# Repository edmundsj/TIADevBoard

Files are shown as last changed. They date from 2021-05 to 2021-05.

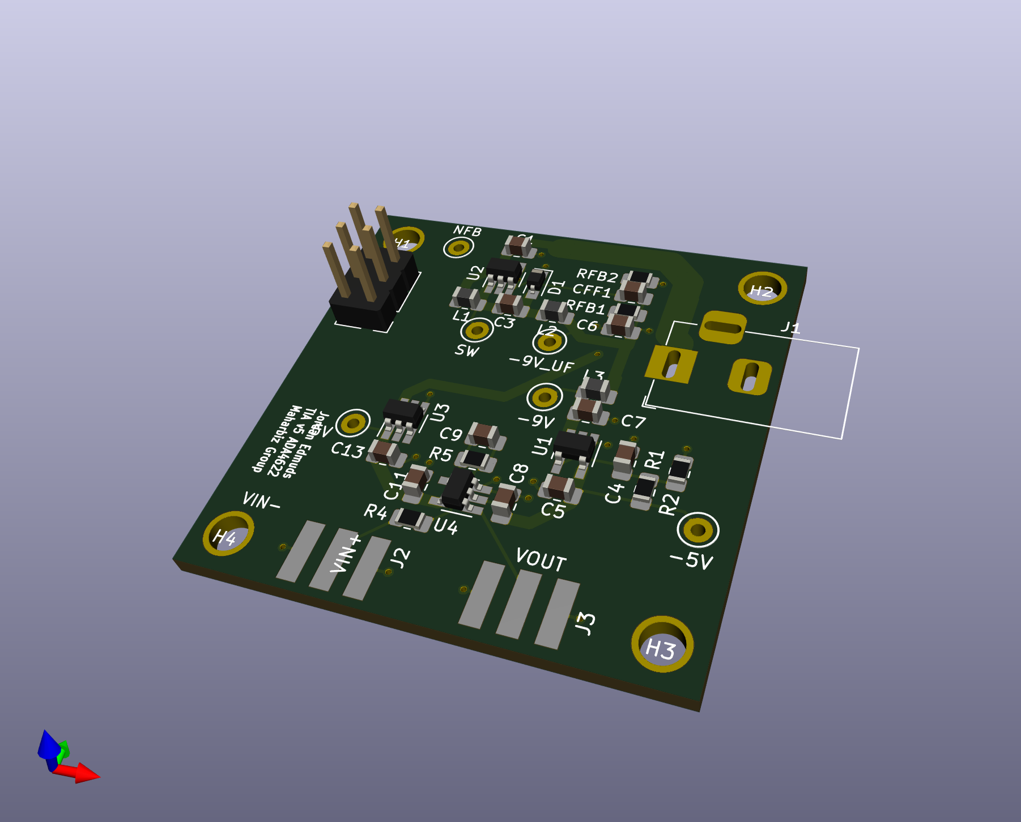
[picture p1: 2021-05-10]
tia_dev_board_3D.png

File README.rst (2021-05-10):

+/-5V TIA Dev Board
=========================

Features
----------
- On-board +/-5V supply generation
- Uses a low-noise opamp: ADA4622 (<1fA/rtHz, <15nV/rtHz)
- Low bias current opamp (<10pA) for accurate DC current measurement
- Opamp is unity gain stable, no input offset (<2uV), common-mode input beyond the rails, R2R output
- SMA input and output
- Low parasitic input/output capacitance

Issues in Versions 1,2
-----------------------
- [FIXED in v3] Old versions of this PCB relied on an off-board +/-15V dual supply, which was coupling in a huge amount of noise into the opamp.
- [FIXED in v3] Old opamp (ADA4625) appears to be often out of stock and is quite expensive (~$10). 

Issues in Version 3
--------------------
- The screw terminal is exerting force on an unspported area of the PCB, I should add another couple of standoffs so this does not happen.
- The -5V input is actually -7.5V. Should use two 3k resistors instead of two 1k resistors
- [FIXED v4] Pin 2 (sense pin) on ADP7183 is not connected to anything. It should be connected to Vout.
- [FIXED v4] There should be a 1uF capacitor to ground hanging off pin VA.
- [FIXED v4] There should be a 10nF capacitor between VA and VFB, not 1uF.

Issues in Version 4
---------------------
- [FIXED v5] Very high output noise (~10uV/rtHz) when driving diode with opamp. Switched to driving with GND.
- [FIXED v5] OPA2387 appears to have ~5x the specced current noise. Switched to ADA4622 (0.7fA/rtHz vs 70). 
- [FIXED v5] Switch back to dual supply with linear regulators
- [FIXED v5] Filter the output of the switched supply with an CLC network
- [FIXED v5] Add bulkhead-mount input/output SMA connectors to enclose entire board in grounded Faraday cage

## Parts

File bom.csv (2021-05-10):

Part Name | Reference | Value | Quantity
Capacitor | C3 | 1uF | 1
Capacitor | C4 | 10nF | 1
Capacitor | C9 | 3pF | 1
Capacitor | C8, C11 | 100nF | 2
Capacitor | C1, C5-C7, C13 | 10uF | 5
Capacitor | CFF1 | 100pF | 1
Diode | D1 | - | 1
DC Jack | J1 | - | 1
SMA Connector | J2, J3 | - | 2
Ground connector | J4 | - | 1
Inductor | L1-L3 | 22uH | 3
Resistor | R1 | 100k | 1
Resistor | R2 | 32k | 1
Resistor | R4 | 0R | 1
Resistor | R5 | 1M | 1
Resistor | RFB1 | 30k | 1
Resistor | RFB2 | 4.7k | 1
Negative regulator | U1 | TPS723 | 1
Boost converter | U2 | LM2611 | 1
5V regulator | U3 | ADP3330-5 | 1
Opamp | U4 | ADA4622 | 1

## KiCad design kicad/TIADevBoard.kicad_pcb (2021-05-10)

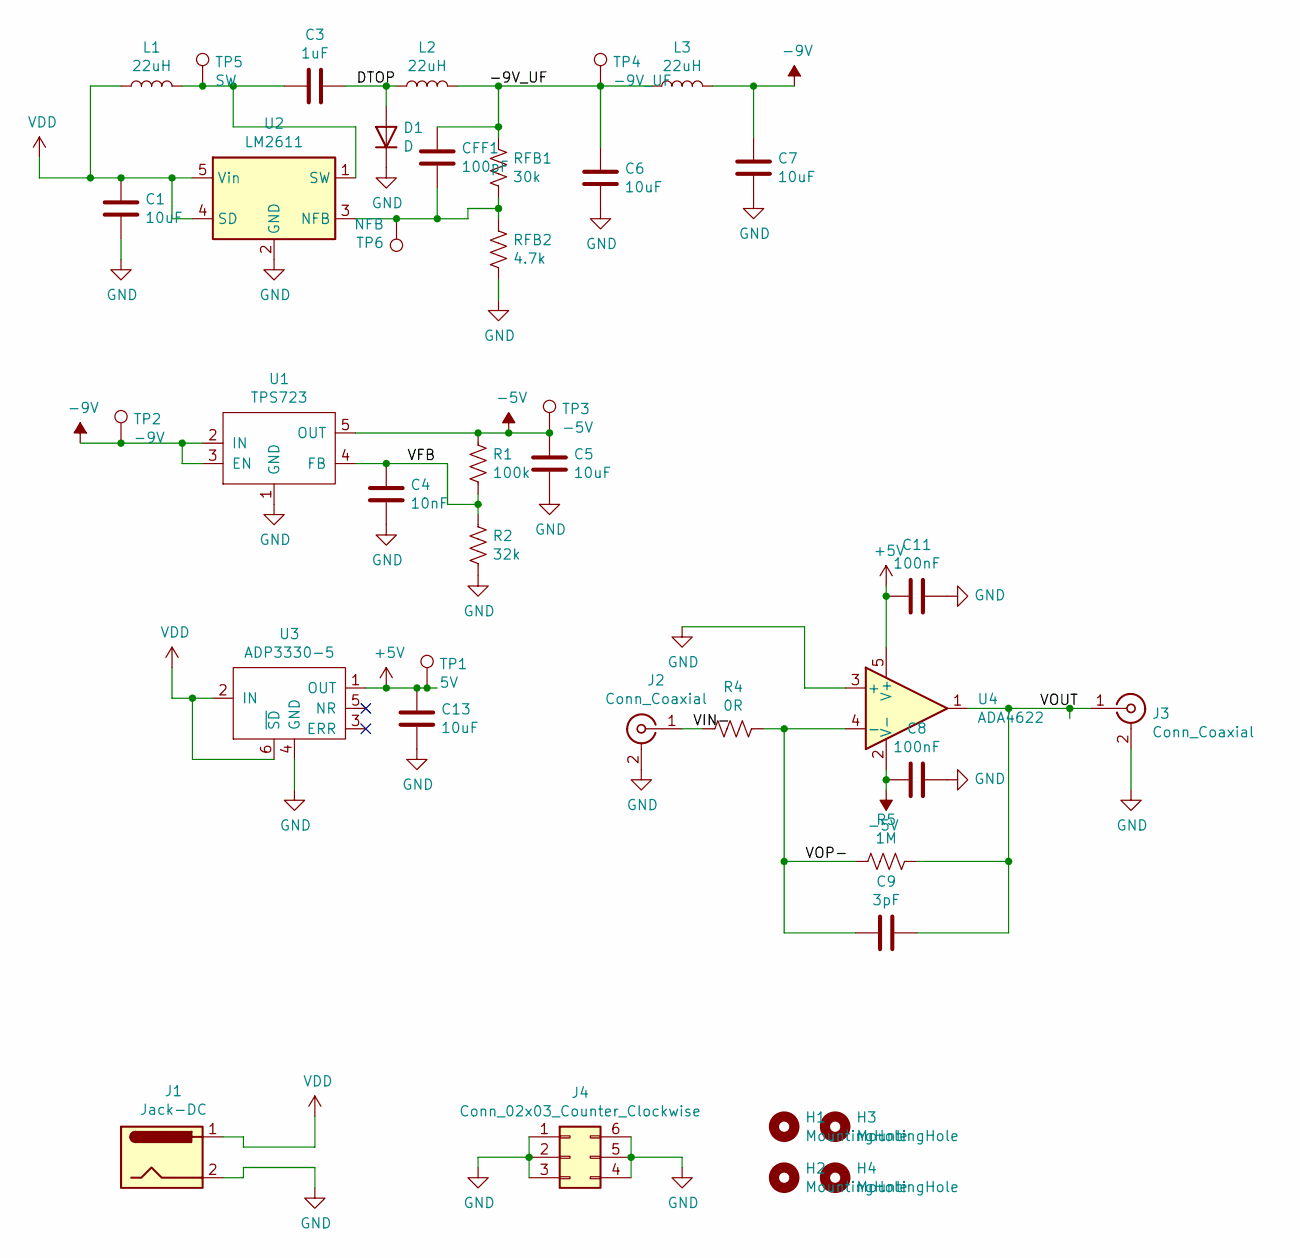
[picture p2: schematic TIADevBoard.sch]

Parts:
C1, C5, C6, C7, C13: 10uF; C_0805_2012Metric_Pad1.15x1.40mm_HandSolder
C3: 1uF; C_0805_2012Metric_Pad1.15x1.40mm_HandSolder
C4: 10nF; C_0805_2012Metric_Pad1.15x1.40mm_HandSolder
C8, C11: 100nF; C_0805_2012Metric_Pad1.15x1.40mm_HandSolder
C9: 3pF; C_0805_2012Metric_Pad1.15x1.40mm_HandSolder
CFF1: 100pF; C_0805_2012Metric_Pad1.15x1.40mm_HandSolder
D1: D; D_SOD-323_HandSoldering
H1, H2, H3, H4: MountingHole; m3_mounting_hole
J1: Jack-DC; BarrelJack_Horizontal
J2, J3: Conn_Coaxial; CON-SMA-EDGE-S
J4: Conn_02x03_Counter_Clockwise; PinHeader_2x03_P2.54mm_Vertical
L1, L2, L3: 22uH; L_0805_2012Metric_Pad1.15x1.40mm_HandSolder
R1: 100k; R_0805_2012Metric_Pad1.15x1.40mm_HandSolder
R2: 32k; R_0805_2012Metric_Pad1.15x1.40mm_HandSolder
R4: 0R; R_0805_2012Metric_Pad1.15x1.40mm_HandSolder
R5: 1M; R_0805_2012Metric_Pad1.15x1.40mm_HandSolder
RFB1: 30k; R_0805_2012Metric_Pad1.15x1.40mm_HandSolder
RFB2: 4.7k; R_0805_2012Metric_Pad1.15x1.40mm_HandSolder
TP1: 5V; TestPoint_Keystone_5000-5004_Miniature
TP2: -9V; TestPoint_Keystone_5000-5004_Miniature
TP3: -5V; TestPoint_Keystone_5000-5004_Miniature
TP4: -9V_UF; TestPoint_Keystone_5000-5004_Miniature
TP5: SW; TestPoint_Keystone_5000-5004_Miniature
TP6: NFB; TestPoint_Keystone_5000-5004_Miniature
U1: TPS723; SOT-23-5_HandSoldering
U2: LM2611; SOT-23-5_HandSoldering
U3: ADP3330-5; SOT-23-6_Handsoldering
U4: ADA4622; SOT-23-5_HandSoldering

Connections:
+5V: C11.2, C13.1, TP1.1, U3.1 (OUT), U4.5 (V+)
-5V: C5.1, C8.2, R1.1, TP3.1, U1.5 (OUT), U4.2 (V-)
-9V: C7.1, L3.2, TP2.1, U1.2 (IN), U1.3 (EN)
/-9V_UF: C6.1, CFF1.1, L2.2, L3.1, RFB1.1, TP4.1
/DTOP: C3.1, D1.2 (A), L2.1
/VFB: C4.1, R1.2, R2.1, U1.4 (FB)
/VIN-: J2.1 (In), R4.2
/VOP-: C9.2, R4.1, R5.2, U4.4 (-)
/VOUT: C9.1, J3.1 (In), R5.1, U4.1
GND: C1.2, C4.2, C5.2, C6.2, C7.2, C8.1, C11.1, C13.2, D1.1 (K), J1.2, J2.2 (Ext), J3.2 (Ext), J4.1, J4.2, J4.3, J4.4, J4.5, J4.6, R2.2, RFB2.2, U1.1 (GND), U2.2 (GND), U3.4 (GND), U4.3 (+)
unnamed: C3.2, L1.2, TP5.1, U2.1 (SW)
unnamed: CFF1.2, RFB1.2, RFB2.1, TP6.1, U2.3 (NFB)
VDD: C1.1, J1.1, L1.1, U2.4 (SD), U2.5 (Vin), U3.2 (IN), U3.6 (~SD)

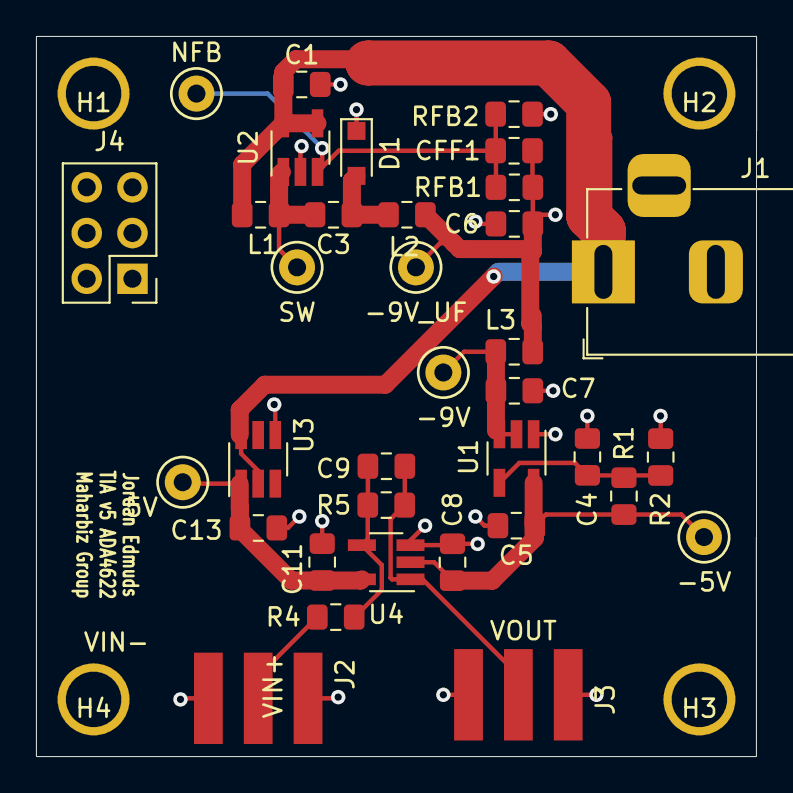
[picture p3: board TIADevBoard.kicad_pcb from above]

Board: 2 copper layers, 40.0 x 40.0 mm, 39 parts (0 on the bottom side), 13 nets.

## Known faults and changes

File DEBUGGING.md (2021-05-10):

# Appendix 1 - Debugging Notes
- I'm pretty sure I fried my -2.5V regulator. With an input of -3.44V, it outputs -1.97V. This is a 1.5V dropout voltage with a target regulation of -2.5V, which indicates I destroyed the thing. It's also completely contaminated with switching noise of magnitude ~40mVpp, which means we aren't regulaating anything. The switching noise at the output of the switching regulator is 120mVpp, and the switching frequency is 6.58kHz. This switching speed seems really low - it would seem to indicate we have a ~3nF timing capacitor, but we have a ~200pF capacitor.
- I will try replacing C7 with a 10nF capacitor and short pin 1 to pin 2, see if that fixes the issues I was having.
- Still getting oscillation when replacing C7 with a 47nF cap and shorting pin 1 and pins 2, although the oscillations are at a much higher frequency (~10x compared to before). I suspect the capacitance value has something to do with this. I added a 1uF capacitor between pin 3 (VA) and ground, connected via a jumper wire. Adding this capacitor caused the oscillations to stop, but the output voltage is -3.3V, not -2.5V, and the regulation is absolute shit. The datasheet says that C7 can be between 10nF and 1uF, so I don't think that's the issue. I think I may just give up on the negative supply. VREG should be at -0.5V but it appears to not be at that voltage, it's actually like 50mV.
- I suspect this has something to do with either the rework conditions (worked at too high of a temperature) or I accidentally ESD'd the chip.
- It may be advisable to switch to just driving the shield to the photodiode with the opamp rather than grounding the shield. Before redesigning the PCB to that effect, I'll try to solder on one more more tomorrow, paying close attention to rework temperature, keeping the rework temperature under 500F, and always keeping myself grounded to avoid frying the chip. That would save considerably on complexity of the PCB and I wouldn't have to use any of these godforsaken QFN packages. The downside is higher impedance driving the shield, but I think that should be fine.
- If the opamp has a biased output (for example at 1.65V) this means that the following stage will need a different offset voltage to bias the ADC properly - that's OK, I can increase the offset from VDD/4 to VDD/2 and this issue should be fixed. This opamp also may not behave properly when driving the cable capacitance. It should work, as I don't expect the parasitic cap to be more than ~100pF. A single supply would work for this just fine, with some voltage division. Yeah, let's just do that.
- Well, at least the voltage inverter worked decently well :) Nowhere close to spec, but it still inverted the voltage.
- We should test the opamp tomorrow to confirm it works as expected.
- The new TIA has higher noise than expected (400nV/rtHz), and, when connected to the photodiode, the noise goes up MASSIVELy to around 60uV/rtHz, even after ensuring the ADC is properly biased. I don't know what the issue is, but it's pretty bad. The guard voltage is correct (1.5V), and the voltage across the diode is very nearly 0V. Less than ~1mV. Either the photodiode does not like being biased in this way, or the TIA is just a heaping pile of shit. I guess for now I'm stuck with my old TIA, as I have no idea what's going on with this one. The 60Hz interferers are still there, indicating the noise is not coming intermittently from the power supply. However, the interferers are completely eliminated by a crappy Faraday cage, which I never achieved with the last TIA. 
- Here's my guess as to why the noise is so high: the output current noise of the opamp is being dropped across the photodiode, which has a very high impedance. If the photodiode were a dummy load with a lower impedance, this would not be the case. The output current noise would only have to be in the ~pA/rtHz range, which is potentially plausible. I can connect a dummy load tomorrow to see if this is indeed the issue. If it is, I'm going to need to rethink how to use a negative supply for this, and how to add a reliable (integrated) Faraday cage to my PCB, completely covering the high-impedance node.
- Apparently what I am really looking for is now a low-noise opamp per se, since this usually means low VOLTAGE noise, but a low input bias current opamp (which implies low current noise). However, the OPA2387 is rated for a bias current of 135pA, which would predict an input current noise density of 7fA/rtHz, which is nowhere close to its spec. Apparently also JFET-based opamps are what I am looking for. This is how I should start my search. I also want an opamp that's specced at the same supply voltages I am plannong on using, and at this point, I'm flexible.
- Ultimately, my problem is that I want an opamp which can operate off a 5V supply (or anywhere near 5V) so I can use a positive and negative supply. The ADA4625 does not work for this because it requires the input common-mode voltage to be 1.5V, not VDD/2, and the output voltage to be VDD/2, which is clearly not tenable if I am operating it as a TIA. It looks like the ADA4622 is an excellent choice. 0.8fA/rtHz current noise, specced at +/-5V operation, 12nV/rtHz voltage noise, and works at Vcm=0V. PSRR is only 80dB, but that's a minimum guaranteed spec, so I'll work with it.
- I found this app note on noise to be quite helpful: https://www.analog.com/media/en/training-seminars/tutorials/MT-047.pdf
- Analog devices recommends using the ADP5070 as the switching regulator, which operates at a whopping 2MHz. Why do they recommend this? What's its benefit over the alternatives?

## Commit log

2021-01-15 added schematic, PCB not routed or laid out. BOM not complete
    [TIADevBoard.kicad_pcb, TIADevBoard.sch]
2021-01-15 Version 3 complete with +3V/-2.5V low noise LDO regulated supplies, a -5V inverting DC switching converter, and a new low-noise TIA
    [TIADevBoard-B_Cu.gbr, TIADevBoard-B_Mask.gbr, TIADevBoard-B_Paste.gbr, TIADevBoard-B_SilkS.gbr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]
2021-01-15 added bill of materials, README
    [TIADevBoard.kicad_pcb, bom.csv]
2021-01-29 added second SMA connector for Vin+ terminal
    [TIADevBoard-B_Cu.gbr, TIADevBoard-B_Mask.gbr, TIADevBoard-B_Paste.gbr, TIADevBoard-B_SilkS.gbr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]
2021-01-29 added 3D image of TIA dev board
2021-02-09 fixed some errors in version 3 of PCB, updated the README to that effect.
    [TIADevBoard.kicad_pcb, TIADevBoard.sch, bom.csv]
2021-02-09 partial redesign of TIA v4, removed boost/buck converter, -2.5V linear regulator, added in second opamp in unity gain configuration with bias voltage. Layout not complete.
    [TIADevBoard.kicad_pcb, TIADevBoard.sch]
2021-02-12 modified TIA dev board to use a single supply of 3.3V, and optionally bias both sides of the diode at VDD/2 using one of the opamps to drive the guard shield. Should work just as well as grounding it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
    [TIADevBoard-B_Cu.gbr, TIADevBoard-B_Mask.gbr, TIADevBoard-B_Paste.gbr, TIADevBoard-B_SilkS.gbr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]
2021-02-18 updated PCB layout to incorporate schematic changes
    [TIADevBoard.kicad_pcb]
2021-02-25 added gerbers for version 5
    [TIADevBoard-B_Cu.gbr, TIADevBoard-B_Mask.gbr, TIADevBoard-B_Paste.gbr, TIADevBoard-B_SilkS.gbr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]
2021-03-12 updated dev board schematic with correct resistor values
    [TIADevBoard.sch]
2021-05-10 updated BOM with new components, moved kicad parts into their own folder
    [TIADevBoard.kicad_pcb, TIADevBoard.sch, bom.csv]
2021-05-10 updated PNG to latest dev board file
